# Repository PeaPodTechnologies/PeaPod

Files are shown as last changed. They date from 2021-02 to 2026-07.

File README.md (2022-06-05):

# PeaPod <!-- omit in toc -->

     

A cloud-connected isolated and automated plant growth environment, able to generate any environment from a combination of independent environment parameters. 

Designed as both a hassle-free food production system and a research tool for precise and distributed mapping of the plant-environment relationship.

<!-- TODO: Build statuses? etc. -->

Submitted to the [NASA/CSA Deep Space Food Challenge](https://impact.canada.ca/en/challenges/deep-space-food-challenge). _Update_: PeaPod has [won](https://impact.canada.ca/en/challenges/deep-space-food-challenge/semi-finalists) Phase 1 and moved on to prototyping for Phase 2!



***

### Table of Contents

- [Background](#background)
  - [Features](#features)
- [Production](#production)
- [Development](#development)
- [Contribution](#contribution)
  - [New Issue](#new-issue)
  - [Existing Issues](#existing-issues)
- [Acknowledgements](#acknowledgements)

<!-- include some visuals, i.e. a 3D GIF of the CAD, maybe a flowchart/diagram -->

***

## Background

See our [requirements document](https://github.com/PeaPodTechnologies/PeaPod/blob/staging/docs/requirements/Requirements.pdf).

### Features

See our [progress report](https://github.com/PeaPodTechnologies/PeaPod/blob/staging/docs/RrogressReport.pdf).

<!-- ### Innovations
PeaPod is *not* a fancy container with a light stand. 

PeaPod can **precisely** replicate climates for optimal growing conditions, and also has the ability to collect plant growth data during the growing cycle. 
This data is then used to further *optimize climate parameters* so food grown in PeaPods will taste better over time.

PeaPod is *modular* and *easy to assemble*. 
Construction with aluminum extrusion allows PeaPods to be transported like IKEA furniture, useful for situations where a lot of food is required at the end of a long journey. 
A lot of PeaPods can be collapsed into a tiny space. 
This also means PeaPods can be configured to be any size to grow any type of plant.

PeaPod is self-optimizing, versatile, easy to assemble, and it makes food. -->

***

## Production

<!-- ### Assembly

### Installation

w/ examples, i.e. GIF of expected output, inline code -->

TBA.

***

## Development
<!-- dependencies, environment, languages -->

> See [`software/README`](software/README.md#Development) and the individual [`subsystems`](/subsystems/README.md) for development details.

<br>

## Contribution

### New Issue

1. Open an issue with the features you'd like to add/bugs you'd like to see squashed (admins will add labels, assignments, etc.)
2. Discuss the scope and specifics in the issue, and either:
   1. Make a new branch, make changes, open a **PR Draft** (if you have permissions); or
   2. Fork this repo, make changes, open a **PR Draft**.
3. Request review by changing the **PR Draft** to a full-blown **PR** when you think it's ready.
4. If the reviewer(s) accept the changes, they will merge the **PR** and close the related issue.

### Existing Issues

Check out our [open issues](https://github.com/PeaPodTechnologies/PeaPod/issues?q=is%3Aopen+is%3Aissue+label%3A%22Status%3A+Open%22)!

<!-- ### Support -->
<!-- issues page, discussion board/Discord? -->

<br>

## Acknowledgements

Sincere thanks to the following individuals and groups:
- MIT Media Lab's Open Agriculture Initiative (for inspiration)
- The Open Source community
- Deep Space Food Challenge administrators and participants

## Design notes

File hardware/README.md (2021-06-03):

# PeaPod Hardware

Includes all bill of materials (BOM), 3D printing files, schematics, etc.

See [ASSEMBLY.md](../docs/assembly/ASSEMBLY.md) for fabrication and assembly instructions.

## References

Documentation for BOM parts can be found on each part's DigiKey page under "Datasheet".

# Development

BOM downloaded from [DigiKey](https://www.digikey.ca) (can be directly uploaded for ordering). 3D model files are made using [AutoDesk Fusion 360](https://shop.prusa3d.com/en/3d-printers/181-original-prusa-i3-mk3s-3d-printer.html). GCODE files are for the [Prusa MK3S+ MMU2](https://shop.prusa3d.com/en/3d-printers/181-original-prusa-i3-mk3s-3d-printer.html) using *Prusament PETG* filament. Schematics and PCB files made using [EasyEDA](https://easyeda.com/).

## Requirements

- Fusion 360 or your 3D editor of choice
- EasyEDA or your PCB/schematic editor(s) of choice
- Excel/Google Sheets or your CSV reader/spreadsheet software of choice

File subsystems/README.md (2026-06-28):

# PeaPod Subsystems

All subsystems will follow the same structure:

- `README.md` - Detailed instructions for fabrication and purchasing, list of materials incl. tools, assembly instructions with graphics, testing and validation protocol, method of operation, and expected results.
- `REQUIREMENTS.md`
- `assets/` - various graphical/etc. assets (diagrams, etc. excluding pictures of schematics/PCB layouts)
- `hardware/`
- `software/`

In addition, each subsystem should have its own `README.MD` with the following info:

- Purchasing
- Assembly w/ photos
- Testing (process and results)

## Hardware

Includes all **reference** bills of materials (BOM), 3D printing files, PCB files, etc.

Subdirectories:

- `boms/` - Bills of Materials (CSV files)
- `fabrication/` - Fabricated part files (i.e. 3D printing files)
- `schematics/` - PCB schematics (.SCH and .BRD files and photos of each)
- `gerber/` - Gerber files (PCB manufacturing)

## Software

Includes all C/C++ libraries and Arduino testing scripts.

Subdirectories:

- `src/` - Libraries
- `tests/` - Test scripts

# Development

Component BOMs downloaded from [DigiKey](https://www.digikey.ca) (can be directly uploaded for ordering). All other BoM types (fabrication, purchase, etc.) copied from the [BoM Templates](/.github/BOM_TEMPLATES/). 3D models, PCB and schematic docs are made using [AutoDesk Fusion 360](https://www.autodesk.ca/en/products/fusion-360/overview).

## Requirements

- Fusion 360 or your 3D editor of choice
- EasyEDA or your PCB/schematic editor(s) of choice
- Excel/Google Sheets or your CSV reader/spreadsheet software of choice

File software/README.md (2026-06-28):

# PeaPodOS <!-- omit in toc -->
 
A two-part system, consisting of a high-level software application and a low-level microcontroller firmware, designed for remote monitoring and configuration of control systems.

The software is written in TypeScript and runs on any compatible computer system with an internet connection, persistent storage, and a UART serial interface (i.e. Raspberry Pi Zero 2 W).

The firmware is written in Arduino C++ and runs on any compatible microcontroller system with UART serial and I2C interfaces (i.e. Adafruit ESP32 Feather V2). See `./microcontroller/README.md` for more information.

Ensure UART voltage levels are compatible (i.e. 3.3V for both Raspberry Pi Zero 2 W and Adafruit ESP32 Feather V2).

### Table of Contents
- [Background](#background)
- [Architecture](#architecture)
- [Development](#development)
- [Production](#production)
  - [Raspberry Pi Zero 2 W](#raspberry-pi-zero-2-w)
    - [SD Card Preparation](#sd-card-preparation)
    - [First-Time Setup](#first-time-setup)
  - [Preparation](#preparation)
  - [Installation](#installation)
  - [Execution](#execution)

# Background

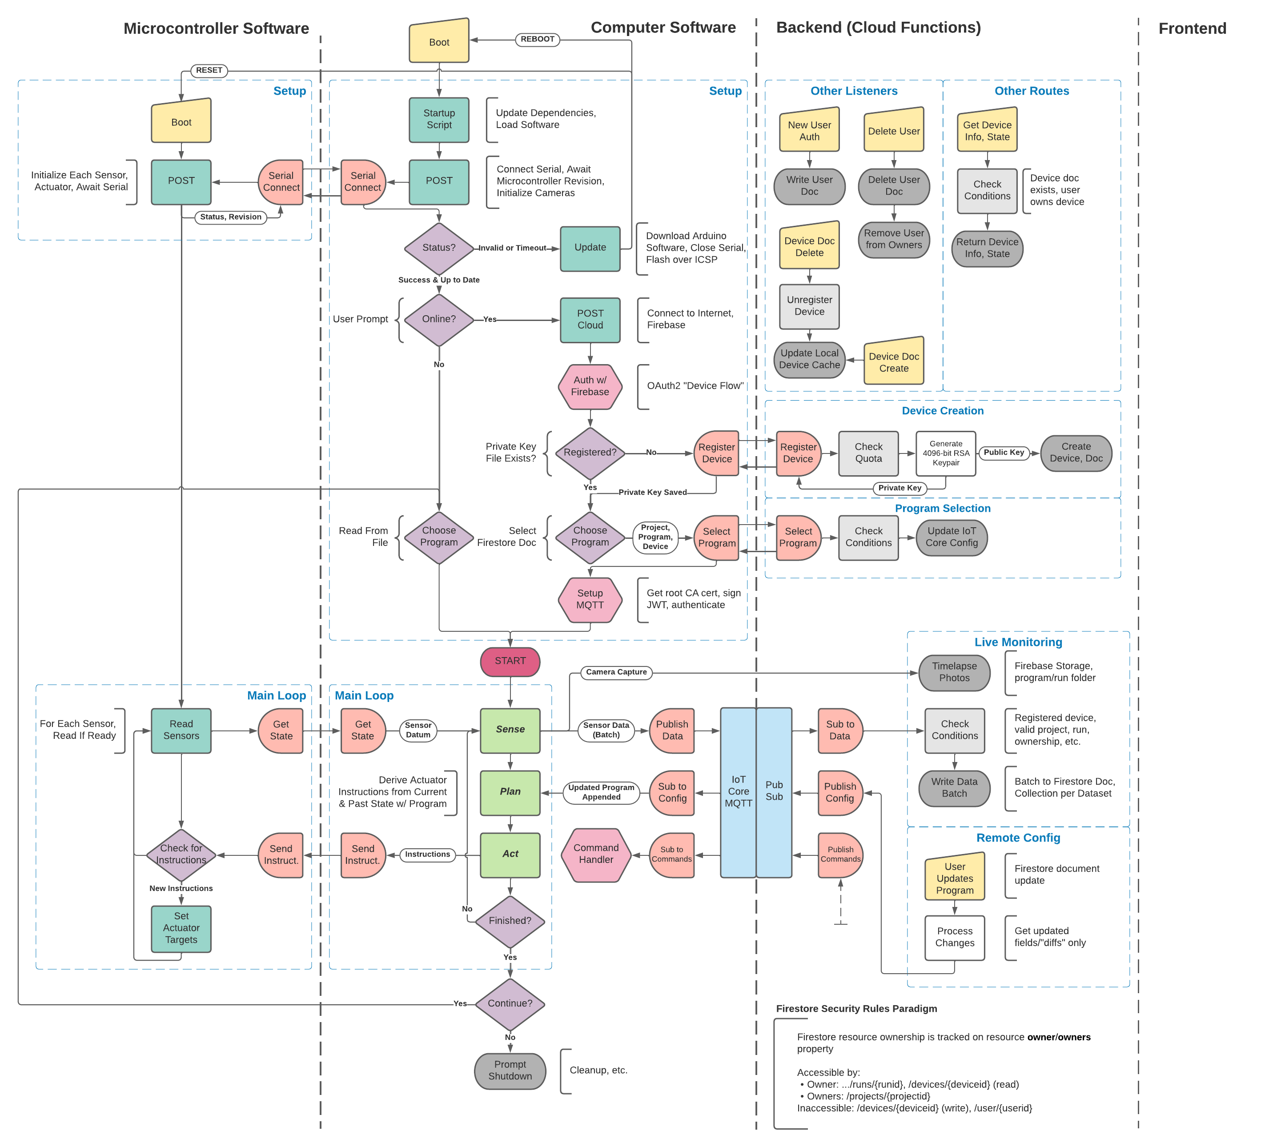
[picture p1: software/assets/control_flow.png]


# Architecture

start menu
- publishing mode selection (Local Filesytem, Firebase, Dashboard)
- Firebase Device Flow Authentication
  - Provider Selection (Google, GitHub)
  - Device Code & URL
- Microcontroller Serial Port Selection

serial communication
- bidirectional
- JSON-formatted
- newline-delimited
- encoding: device commands, system configuration
- decoding: telemetry/debugging

WebSockets API w/ Callbacks
- camera capture and image streaming
- serial passthrough
- intervals
- linker
- firmware flashing
- scheduler

Control Systems (TODO)

dashboard webserver
- Debugging Console
- Telemetry Charts
- Calendar + DataGrid
- Interval & Event Scheduler
    - Microcontroller Instructions
    - Tasks

# Development

# Production

## Raspberry Pi Zero 2 W

### SD Card Preparation

The following are performed on a computer with an internet connection:

1. Format a microSD card (>=32GB) with a single FAT partition.
2. Download the Raspberry Pi Imager [(Download)](https://www.raspberrypi.com/software/).
3. Flash the SD card with a *Raspberry Pi OS Lite (64-bit)* image.

> Note: A custom PeaPodOS image will be released in the future.

### First-Time Setup

4. Plug in a keyboard and display, insert the microSD card, and power on the Raspberry Pi Zero 2 W.

The following are performed on the Raspberry Pi Zero 2 W, with a keyboard and monitor:

5. Login.
6. Execute `sudo raspi-config` and perform these steps to setup the Pi:
   1. *System Options > Wireless Lan* - Setup WiFi and connect to the Internet (if not set from within imager)
   2. *System Options > Hostname* - Set a unique hostname, e.g. `peapod` (if not set from within imager)
   3. *System Options > Boot/Auto Login* - Select `Console Autologin` (B2)
   4. *Interface Options > SSH* - `Enable` SSH Server (if not set from within imager)
   5. *Interface Options > Serial Port* - `Disable` serial login shell, but `Enable` the serial port hardware
   6. *Performance Options > GPU Memory* - 256 MB (to support the camera module, if used)
   7. *Localisation Options > Locale* (i.e. `en_US.UTF-8`)
   8. *Localisation Options > Timezone* (i.e. `US` > `Eastern`)
   9. *Localisation Options > Keyboard* (i.e. `Generic 105-key` > `English (US)` > `Default` > `No compose key`)
   10. Optional: *Advanced Options > Expand Filesystem*
   11. Reboot to save: `sudo reboot -f` 

> You can now SSH into the Raspberry Pi to perform the rest of the setup, or continue with the keyboard and monitor.

## Preparation

The following are performed on a computer with an internet connection:

7. Execute `./scripts/build.sh` WITH NO ARGUMENTS to compile TypeScript to JavaScript and bundle the webserver, creating an `./out.tar.gz` archive containing the compiled software.
8. Execute `./scripts/upload.sh <hostname>` to upload the `./out.tar.gz` archive to the Raspberry Pi Zero 2 W home directory, where `<hostname>` is the hostname of the Raspberry Pi (e.g. `peapod.local`).

> You may need to use `chmod +x ./scripts/*.sh` to make the scripts executable.

## Installation

9. Update package listings, upgrade existing packages: `sudo apt update && sudo apt full-upgrade -y`

10. Install Node.JS, the Node package manager, and Python dependencies: `sudo apt install -y nodejs npm python3-venv python3-dev`
<!-- 3. Install main software package: `sudo npm i -g @peapodtech/peapodos --save` -->
<!-- 4. If using a Raspberry Pi Camera, install the camera package: `sudo apt install -y libcamera-apps` -->

11. Install [PlatformIO Core](https://docs.platformio.org/en/latest/core/installation/methods/installer-script.html#super-quick-macos-linux)
<!-- 
1. Create a custom configuration file for the AVR flash utility *avrdude* to be able to program the Arduino Nano via ICSP over the Raspberry Pi's GPIO pins:
   1.  Create a local copy of the *avrdude* configuration file with `cp /etc/avrdude.conf ~/avrdude_gpio.conf`, then modify your copy with `nano ~/avrdude_gpio.conf`. Copy the following to the end of the file:

       ```
       # Raspberry Pi GPIO configuration for avrdude.
       programmer
         id    = "peapod";
         desc  = "Use the Linux sysfs interface to bitbang GPIO lines";
         type  = "linuxgpio";
         reset = 5;
         sck   = 6;
         mosi  = 12;
         miso  = 13;
       ;
       ```
       (*Ctrl-O* to save, *Ctrl-X* to exit)
   2.  Verify the configuration and connection to the Arduino with `sudo avrdude -p m328p -C/avrdude_gpio.conf -c peapod -v`. A successful output should look something like:
       ```
       avrdude: Version 6.3-20171130
            Copyright (c) 2000-2005 Brian Dean, http://www.bdmicro.com/
            Copyright (c) 2007-2014 Joerg Wunsch

            System wide configuration file is "/home/pi/avrdude_gpio.conf"
            User configuration file is "/root/.avrduderc"
            User configuration file does not exist or is not a regular file, skipping

            Using Port                    : unknown
            Using Programmer              : peapod
            AVR Part                      : ATmega328P
            Chip Erase delay              : 9000 us
            PAGEL                         : PD7
            BS2                           : PC2
            RESET disposition             : dedicated
            RETRY pulse                   : SCK
            serial program mode           : yes
            parallel program mode         : yes
            Timeout                       : 200
            StabDelay                     : 100
            CmdexeDelay                   : 25
            SyncLoops                     : 32
            ByteDelay                     : 0
            PollIndex                     : 3
            PollValue                     : 0x53
            Memory Detail                 :

                                     Block Poll               Page                       Polled
              Memory Type Mode Delay Size  Indx Paged  Size   Size #Pages MinW  MaxW   ReadBack
              ----------- ---- ----- ----- ---- ------ ------ ---- ------ ----- ----- ---------
              eeprom        65    20     4    0 no       1024    4      0  3600  3600 0xff 0xff
              flash         65     6   128    0 yes     32768  128    256  4500  4500 0xff 0xff
              lfuse          0     0     0    0 no          1    0      0  4500  4500 0x00 0x00
              hfuse          0     0     0    0 no          1    0      0  4500  4500 0x00 0x00
              efuse          0     0     0    0 no          1    0      0  4500  4500 0x00 0x00
              lock           0     0     0    0 no          1    0      0  4500  4500 0x00 0x00
              calibration    0     0     0    0 no          1    0      0     0     0 0x00 0x00
              signature      0     0     0    0 no          3    0      0     0     0 0x00 0x00

            Programmer Type : linuxgpio
            Description     : Use the Linux sysfs interface to bitbang GPIO lines
            Pin assignment  : /sys/class/gpio/gpio{n}
              RESET   =  8
              SCK     =  11
              MOSI    =  10
              MISO    =  9

       avrdude: AVR device initialized and ready to accept instructions

       Reading | ################################################## | 100% 0.00s

       avrdude: Device signature = 0x1e950f (probably m328p)
       avrdude: safemode: lfuse reads as FF
       avrdude: safemode: hfuse reads as DA
       avrdude: safemode: efuse reads as FD

       avrdude: safemode: lfuse reads as FF
       avrdude: safemode: hfuse reads as DA
       avrdude: safemode: efuse reads as FD
       avrdude: safemode: Fuses OK (E:FD, H:DA, L:FF)

       avrdude done.  Thank you.
       ``` -->

<!-- 11. Edit the `sudoers` file to allow `avrdude` to be executed using `sudo` *without a password*:
    1.  Open the `sudoers` file: `sudo visudo`
    2.  Add the following line to the end (assuming your username is `pi`, the hostname is `peapod`, and the `avrdude` binary is located at `/usr/bin/avrdude`):
        
        `pi peapod = (root) NOPASSWD: /usr/bin/avrdude`
        
        (*Ctrl-O* to save, *Ctrl-X* to exit; *avrdude* can be located with `whereis avrdude`) -->

<!-- 12. Install the *UV4L* camera library:
    1.  `curl https://www.linux-projects.org/listing/uv4l_repo/lpkey.asc | sudo apt-key add -`
    2.  Add the package listings: `echo "deb https://www.linux-projects.org/listing/uv4l_repo/raspbian/stretch stretch main" | sudo tee /etc/apt/sources.list.d/uv4l.list`
    3.  Update packages: `sudo apt-get update`
    4.  Install the core library, the Raspberry Pi driver, extra scripts, adn WebRTC support: `sudo apt-get install uv4l uv4l-raspicam uv4l-raspicam-extras uv4l-webrtc-armv6` -->

12.  Populate a `~/.env` file based on `./.env.template` with Firebase configuration, Google and/or GitHub auth configuration, serial port configuration, and webserver configuration (if applicable).

13. Unpack the `~/out.tar.gz` archive to the home directory: `tar -xzf ~/out.tar.gz -C ~`

14. Connect a USB cable from the computer (i.e. Raspberry Pi Zero 2 W) to the microcontroller (i.e. Adafruit ESP32 Feather V2), and verify that the serial port is available and openable by executing `node ~/serialtest.mjs` and following the prompts. The serial port should be something like `/dev/ttyACM0` (NOT `/dev/ttyS0`, this is the GPIO UART).

15. Perform first-time microcontroller firmware flashing by executing `node ~/flash.mjs` and following the prompts. The serial port should be something like `/dev/ttyACM0` (NOT `/dev/ttyS0`, this is the GPIO UART).

## Execution

16. Run the main program by executing `node ~/server.mjs`.

18. Follow the prompts to select a publishing mode (Local Filesystem, Firebase, and/or Dashboard), and if applicable, perform Firebase Device Flow Authentication.

19. The webserver should start, making the dashboard accessible at the displayed hostname and port.

20. Select the appropriate serial port (i.e. `/dev/ttyS0` for GPIO UART-Arduino `Serial1`, `/dev/ttyACM0` for USB-Arduino `Serial`) to connect to the microcontroller.

21. The console will begin printing raw telemetry and debugging information from the microcontroller.

<!-- https://github.com/nebrius/raspi-io/wiki/Getting-a-Raspberry-Pi-ready-for-NodeBots#configuring-your-app-to-start-on-startup -->

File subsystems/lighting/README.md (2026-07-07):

# PeaPod Lighting Subsystem

See `./REQUIREMENTS.md` for the subsystem requirements.

Provides controlled light to the plant canopy and supports programmable photoperiods (on/off), light intensity (dimming), and spectral channel control via Adafruit PCA9685 PWM dimming of MEAN WELL LDD-L constant-current LED drivers powering CREE XLAMP LEDs with a variety of spectra, including PAR and white for imaging. Power regulator, I2C cables, and PCBs are documented swappable components.

# Production

## Assembly

### Bills of Materials

<!-- TODO: Cables?? -->

See `./hardware/lighting_bom_purchase.csv` for the purchase bill of materials. See `./hardware/gerber/` for PCB manufacturing files (NOTE: STENCIL NECESSARY). See `./hardware/lighting_bom_components.csv` for the electronic components bill of materials (DigiKey).

1. 1 x Lighting BOM Components per led board
2. 1 x Lighting BOM Purchase per led board

### Tools and Equipment

Required:
- Soldering Iron, Solder, and Flux
- Wire Strippers (20-30 AWG)
- Reflow Oven (or hot air rework station) and solder paste
- Putty Scraper

Optional, but recommended:
- Helping Hands (for soldering)
- Multimeter (for testing connections)
- Oscilloscope (for testing signal integrity)
- Luminous Flux Meter (for measuring light output)

## Instructions

1. Using a putty scraper, apply solder paste to the PCB using the stencil.
2. Place the surface-mount components (signal connector, resistor, and LEDs) on the PCB according to the silkscreen.
3. Reflow the PCB in a reflow oven (or use a hot air rework station) to solder the surface-mount components.
4. Solder the through-hole components (power connector and LED driver) to the PCB according to the silkscreen.

## Testing

### Power Test

**Protocol**: Connect the 24V power supply (+24VDC and GND) to the power connector on the PCB.

**Validation**: Nothing happens. Test points TP3 and TP4 read +24V and 0V, respectively.

**Failure Protocol**: 

1. *Smoke, Sparks or Unusual Heat/Odors*: Immediately disconnect the power supply. Check the PCB for solder bridges or shorts. If issue persists, check the power supply and ensure it is functioning correctly.

2. *Incorrect Voltage Readings*: Check the power supply connections and ensure the PCB is properly soldered.

### LED Light Test

**Protocol**: Connect the 24V power supply (+24VDC and GND) to the power connector on the PCB. Flash an Arduino-compatible microcontroller with the `./software/tests/Test_SingleWave/Test_SingleWave.ino` sketch. Connect the microcontroller to the signal connector on the PCB (Digital Pin 3 and GND). Observe the behavior of the LEDs.

**Validation**: The LEDs should light up in a sinusoidal wave pattern, with the brightness varying smoothly over time.

**Failure Protocol**: Check the power supply connections and ensure the PCB is properly soldered. Check test points TP3 and TP4 for correct voltage levels. Check the microcontroller connections to the signal connector and ensure the correct pin is used. Check test point TP5 for PWM signal using an oscilloscope. If issue persists, check the microcontroller code and ensure it is functioning correctly.

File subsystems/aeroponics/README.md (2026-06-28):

# Aeroponics Subsystem

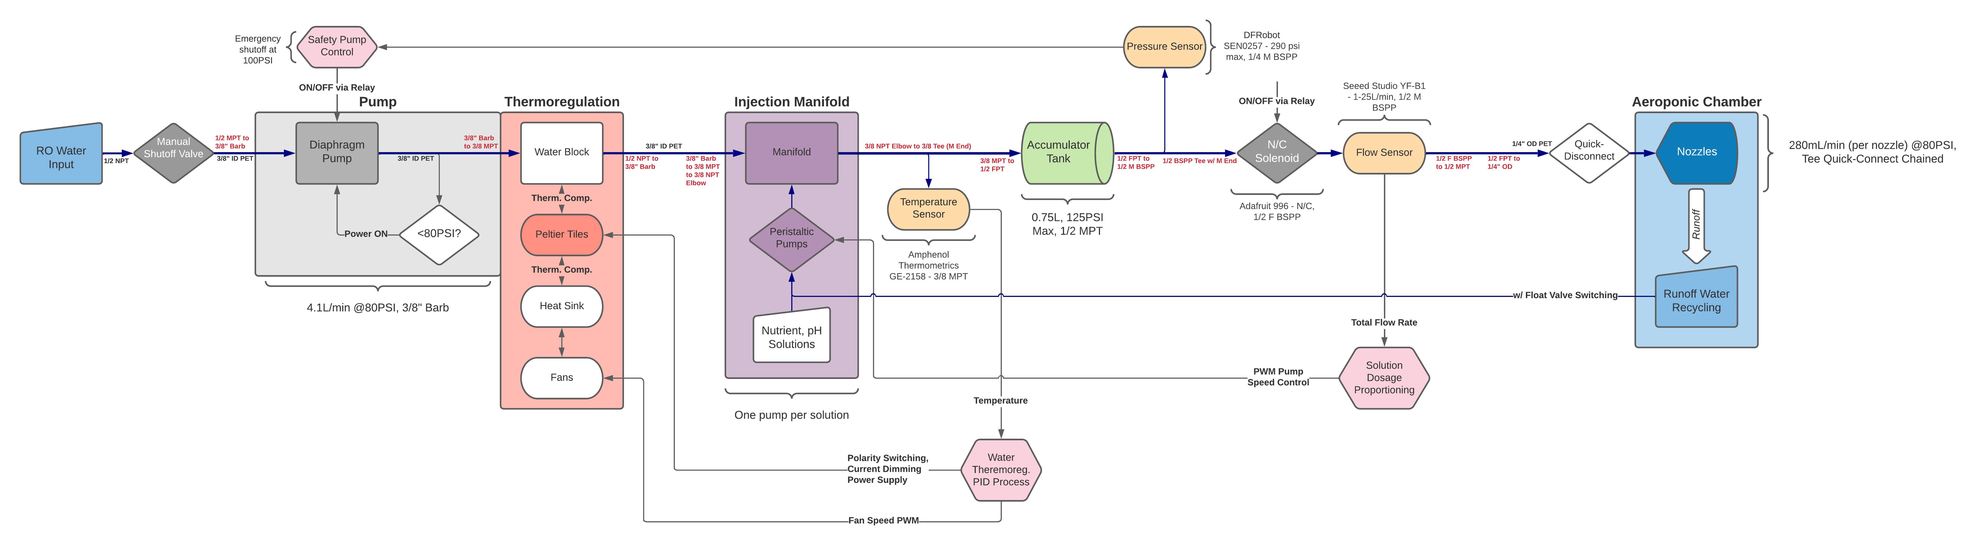
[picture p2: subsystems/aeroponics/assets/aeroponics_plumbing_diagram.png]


# Assembly

## Assembly Notes

Review these before assembly.

- Applying Teflon Tape: [Tutorial](https://www.youtube.com/watch?v=f7mjyzfB9Ec)
- Assembling Compression Fittings: [Instructions](https://www.siouxchief.com/docs/default-source/technical-documents/installations/specialties/ander-lign-fittings-brass) (see pg. 2, Ander-Lign Universal Fittings)

## Materials

### Purchased

Refer to [the purchase BOM](./hardware/aeroponics_bom_purchase.csv).

### Tools

- Cutters (for tubing)
- Utility Knife (for Teflon)
- Pipe Wrench (for fittings)
- 12V Power Supply (for pump testing)

## Instructions

<!-- TODO: tubing lengths -->

> **NOTE**: Refer to the assembled photo below for orientations.

1. Cut a 30cm length of 3/8" PET tubing. Slide two hose clamps onto the tubing. Affix one end to the 3/4" Hose Female x 3/8" Barb fitting (**barb end**), and the other to the 3/8" *input* barb of the diaphragm pump (see photo). Secure one clamp firmly on each end.
3. Apply Teflon tape to the 3/8" Barb x 3/8" MPT Adapter (**MPT end**). Fit this adapter to the 1/2" x 3/8" FPT Coupling (**3/8" ends**). This assembly is now referred to as the *3/8"-1/2" Adapter*.
5. Cut a 30cm length of 3/8" PET tubing. Slide two hose clamps onto the tubing. Affix one end to the 3/8" *output* barb of the pump (see photo), and the other to the 3/8"-1/2" Adapter (**barb end**). Secure one clamp firmly on each end.
6. Cut a 30cm length of 1/4" OD PET tubing. Apply Teflon tape to the 1/4in. OD x 1/2in. MPT Compression Fitting Adapter (**MPT end**). *__DO NOT__ apply to the compression threads.* Assemble the compression fitting to the length of tubing. *__DO NOT__ over-tighten the compression nut.* Fit this adapter (**1/2" end**) to the 1/2" x 1/2" FPT Coupling. This assembly is now referred to as the *1/2"-1/4" OD Adapter*.
4. Apply Teflon tape to both 1/2" MPT ends of the accumulator tank. Affix the 3/8"-1/2" Adapter to the *input barb* of the accumulator tank. Affix the 1/2"-1/4" OD Adapter to the *output barb* of the accumulator tank.
5. Cut two 50cm lengths of 1/4" OD PET tubing. Insert the tubing from the 1/2"-1/4" OD Adapter into the push-connect input of the solenoid. Insert the first length of tubing into a) the push-connect output of the solenoid, and b) one of the "in-line" ends of a push-connect T-fitting. Insert the second length of tubing into a) the opposing "in-line" end of the push-connect T-fitting, and b) one end of a push-connect straight fitting.
6. Insert two nozzles into the open spots on the two push-connect fittings.

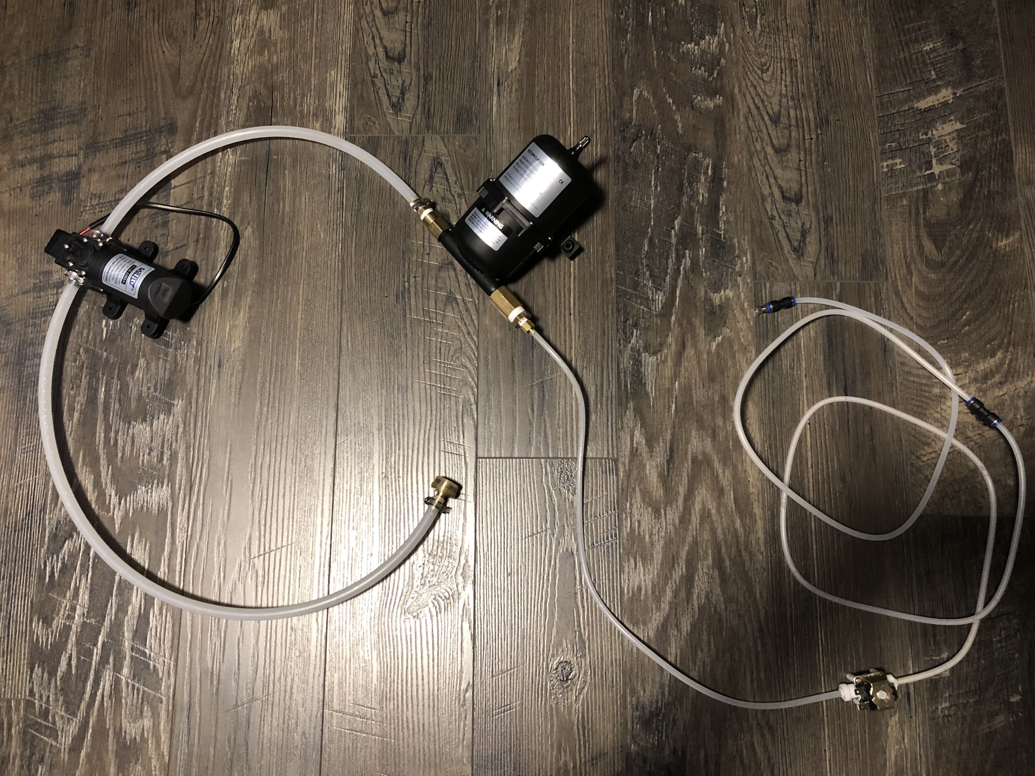
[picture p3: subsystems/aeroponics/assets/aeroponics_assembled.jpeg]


# Testing

> NOTE: As this is a pressurized system, the following tests should be done *in order*. Following the execution of each testing protocol, return the subsystem to the state following the completion of the assembly.

## Leaks

**Protocol**: Detach the solenoid and subsequent components. Attach a standard garden hose to the input end of the system. Turn on the water gradually, checking for leaks at each connection.

**Validation**: No leaks observed at any connection.

**Failure Protocol**: Disassemble the failed connection(s). Remove existing Teflon. Reapply Teflon, and reassemble the connection(s). Ensure Teflon is applied properly, and each connection is appropriately secured.

## Priming

**Protocol**: Fill a bucket with contaminant- and debris-free water. Ensure the system is on level ground. Place the input end of the system in the bucket. Detach the solenoid from the preceding tubing section. Detach the subsequent tubing section from the T-fitting. Connect the tank output tubing section to the T-fitting. Apply 12V power to the pump. *Priming may take a minute or two.*

**Validation**: The pump is able to prime the system and expel all air.

**Failure Protocol**: Ensure the system is level and the system input is submerged. Ensure the pump is receiving power.

## Pressurization

**Protocol**: Same as [Priming](#priming).

**Validation**: The system pressurizes without failure or leak at any connection or component.

**Failure Protocols** (in increasing order of severity): 

1. *Leak*: Depressurize the system. Disassemble the failed connection(s). Remove existing Teflon. Reapply Teflon, and reassemble the connection(s) tightly. Ensure Teflon is applied properly, and each connection is appropriately secured.
2. *Component Failure*: Replace the failed component. Repeat Assembly.

## Nozzle Function

**Protocol**: Same as [Priming](#priming).

**Validation**: Nozzle flow is uninterrupted and consistent in rate over time. Droplet size is as expected and consistent, both over time and across the range of droplets.

**Failure Protocol**: N/A

## Pump Auto-Shutoff

**Protocol**: Same as [Priming](#priming).

**Validation**: Pump shuts off automatically approximately one minute after priming is complete once pressurization is achieved. Nozzle flow is uninterrupted. Pump turns back on automatically to maintain pressure.

**Failure Protocol**: N/A

<!-- TODO: pressure sensor for accuracy -->

<!-- TODO: solenoid function -->

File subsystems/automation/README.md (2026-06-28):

# PeaPod Automation Subsystem

# Assembly

## Materials

### Purchased

See `./hardware/automation_bom_purchase.csv` for the purchase bill of materials. See `./hardware/gerber/` for PCB manufacturing files. See `./hardware/automation_bom_components.csv` for the electronic components bill of materials (DigiKey).

### Tools

Required:
- Soldering Iron, Solder, and Flux
- Wire Strippers (20-30 AWG)

Optional, but recommended:
- Helping Hands (for soldering)
- Multimeter (for testing connections)
- Oscilloscope (for testing signal integrity)

## Instructions

1. Solder stacking headers to the motherboard: one 2x20 at U1 for the Raspberry Pi Zero 2 W, and one each 1x16 and 1x12 at U2 for the Adafruit ESP32 Feather V2.
2. Solder 2x20 stacking header pins to the Raspberry Pi Zero 2 W, ensuring the pins are oriented to connect with the motherboard headers.
3. Solder 1x16 and 1x12 stacking header pins to the Adafruit ESP32 Feather V2 (if not pre-assembled), ensuring the pins are oriented to connect with the motherboard headers.
4. Prepare the micro-SD card according to the instructions in `/software/README.md` (using the SD card adapter). Insert the micro-SD card into the Raspberry Pi Zero 2 W.
5. Insert the Raspberry Pi Zero 2 W and Adafruit ESP32 Feather V2 into their respective headers on the motherboard, ensuring proper orientation (match footprint to the silkscreen).
6. Flash the Adafruit ESP32 Feather V2 with the `/software/microcontroller/` firmware according to the instructions in `/software/README.md`.
7. Assemble all subsystem modules in accordance with their instructions. Cut and strip four Qwiic wires, making eight one-ended connectors. Connect the modules to the Adafruit ESP32 Feather V2 I2C port using Adafruit Qwiic cables.
8. Optional: Mount the Adafruit 7-Segment Display Featherwing directly to the Adafruit ESP32 Feather V2 stacking headers.
9. Attach the small end of the orange-colored camera flex cable to the Raspberry Pi Zero 2 W camera port. Attach the large end to the coupling board. Attach one end of the long camera flex cable to the coupling board, and the other end to the camera module. Ensure that all cables are oriented such that the metal connectors on the cable are facing the PCB.
10. Connect a display to the mini-HDMI port on the Raspberry Pi Zero 2 W.
11. Connect the USB hub to the micro-USB port labelled "USB" on the Raspberry Pi Zero 2 W. Connect the keyboard to the USB hub.
12. Connect the power supply to the micro-USB port labelled "PWR" on the Raspberry Pi Zero 2 W.

# Testing

## Power-On Test

**Protocol**: Power on the system. Observe the behavior of the Raspberry Pi Zero 2 W via the connected display. Observe the behavior of the Adafruit ESP32 Feather V2 via the built-in LED (and 7-segment display and/or LCD display, if applicable).

**Validation**: The Raspberry Pi Zero 2 W boots successfully, as evidenced by the display output. The Adafruit ESP32 Feather V2 boots successfully, as evidenced by the LED behavior. 7-segment display and/or LCD display show expected output (if applicable): variable readout and "PeaPod Initializing...", respectively.

**Failure Protocol**: 

1. *Raspberry Pi Zero 2 W Fails to Boot*: Check power supply connection and ensure the micro-SD card is properly inserted. If issue persists, format and flash the micro-SD card according to the instructions in `/software/README.md` and repeat testing.
2. *Adafruit ESP32 Feather V2 Fails to Boot*: Check connections to the motherboard and ensure the board is properly seated in the header. If issue persists, reflash the Adafruit ESP32 Feather V2 using the appropriate firmware and repeat testing.

## Serial Communication Test

**Protocol**: Execute `yarn buildapi && node serialtest.mjs`. Select the appropriate serial port for the Adafruit ESP32 Feather V2 when prompted. Observe the output in the terminal.

**Validation**: The terminal outputs JSON-formatted sensor data at regular intervals (e.g. every second), as sent from the Adafruit ESP32 Feather V2.

**Failure Protocol**: 

1. *Serial Open Fails*: Check wiring connections to the motherboard and ensure the Adafruit ESP32 Feather V2 is properly seated in the header. Ensure no other applications are using the same serial port.
2. *No Data*: Check that the Adafruit ESP32 Feather V2 is running the appropriate firmware and is programmed to send serial data to the appropriate interface (i.e. Serial for USB vs. Serial1 for RX/TX UART). Check wiring connections to the motherboard and ensure the Adafruit ESP32 Feather V2 is properly seated in the header.

## Camera Test

**Protocol**: Execute `libcamera-hello -t 0`. Observe the output in the terminal and the connected display.

**Validation**: The terminal outputs a continuous stream of camera data, and the connected display shows the camera feed in real time.

**Failure Protocol**: Check camera flex cable connections to the Raspberry Pi Zero 2 W and coupling board, ensuring proper orientation. Ensure the camera module is properly connected to the coupling board. Check that the camera module is functional (e.g. by testing with another Raspberry Pi or camera board, if available). Ensure that the camera interface is enabled in the Raspberry Pi configuration settings.

## Firmware Flash Test

**Protocol**: Execute `pio run -t upload`. Observe the output in the terminal.

**Validation**: The terminal outputs messages indicating successful compilation and upload of the firmware to the Adafruit ESP32 Feather V2.

**Failure Protocol**:
1. *Compilation Fails*: Check that PlatformIO is properly installed and configured. Ensure that the correct board and environment are selected in the `platformio.ini` file. Review error messages for specific issues (e.g. missing libraries, syntax errors) and address accordingly.
2. *Upload Fails*: Check connections to the motherboard and ensure the Adafruit ESP32 Feather V2 is properly seated in the header. Ensure the correct serial port is selected for uploading. Check that the Adafruit ESP32 Feather V2 is in the appropriate mode for flashing (e.g. boot mode) and that any necessary drivers are installed.

## Dashboard Test

**Protocol**: Execute `yarn start`. Observe the output in the terminal and the connected display, and respond to prompts in the terminal as necessary to initiate the dashboard. Using a separate device on the same network, navigate to the appropriate local IP address and port number for the dashboard (e.g. `http://192.168.X.X:3000`). Observe the dashboard behavior and data readouts.

**Validation**: The terminal outputs messages indicating successful connection to the Adafruit ESP32 Feather V2 and receipt of sensor data. The separate device successfully loads the dashboard webpage, which displays real-time sensor data and updates appropriately.

**Failure Protocol**:
1. See *Serial Communication Test* failure protocols for issues related to serial communication between the Raspberry Pi Zero 2 W and Adafruit ESP32 Feather V2.
2. *Dashboard Fails to Load*: Ensure the separate device is on the same network as the Raspberry Pi Zero 2 W. Check that the correct local IP address and port number are being used to access the dashboard. Check for any firewall settings that may be blocking access to the port.
3. *Dashboard Loads but No Data*: Check the terminal output for any errors related to receiving or processing data from the Adafruit ESP32 Feather V2.

## Scheduler Test

**Protocol**: Execute `yarn start` and launch the dashboard. Add Event and Interval tasks using the floating action button with a plus icon. Observe the terminal output for scheduled task execution messages.

**Validation**: The terminal outputs messages indicating the execution of scheduled tasks at the appropriate times. States on the ESP32 Feather V2 change accordingly, as evidenced by the terminal output and dashboard readouts and hardware behaviour.

**Failure Protocol**:
1. *Tasks Not Executing*: Check that the scheduler code is properly implemented and that tasks are being added to the schedule correctly. Review terminal output for any errors related to task scheduling or execution.
2. *States Not Changing*: Check that the scheduled tasks are correctly sending commands to the Adafruit ESP32 Feather V2 and that the firmware on the Adafruit ESP32 Feather V2 is properly set up to receive and respond to these commands. Check wiring connections to the motherboard and ensure the Adafruit ESP32 Feather V2 is properly seated in the header.

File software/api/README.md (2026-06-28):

# API

- Node.JS Console i.e. limited-input devices
- WebSockets, SQL, File Logging, Firebase, etc.
-

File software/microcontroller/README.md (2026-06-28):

# PeaPod Microcontroller Firmware

Makes use of I2CIP, FSM, and DebugJson libraries for QOS-2 I2C device state management and abstraction, program state and control flow, and bidirectional JSON-formatted newline-delimited serial communication, respectively. Supports a main menu via 16x2 character LCD and rotary encoder with push button, and a seven segment display.

# Architecture

## Main

**Globals**:
- Menu State (menu index: enum, submenu index: unsigned char, selected module index: unsigned char)
- FSM:
  - Chronograph
- I2CIP:
  - modules\[8\]
  - errlev\[8\]

**Setup**:

1. Initialize Serial communication (115200 baud).
2. Wait for Serial connection.
3. Instantiate PeaPod modules (Air, Watering, Lighting; See Module Callbacks).
4. Instantiate non-module devices:
   1. Seven-Segment Display (HT16K33)
   2. 16x2 Character LCD (JHD1313)
   3. Rotary Encoder with Push Button (Adafruit Seesaw)
5. Attach LCD print callback to menu state changes.
6. Print firmware `revision` to Serial.
7. Register callbacks:
   1. Cycle Callback (triggered on `Cycle` change):
      1. Set Chronograph to current time.
      2. Calculate and set `FPS`.
      3. Read Serial input (DebugJson) and route commands/config.
   2. Heartbeat Callback (Chronograph interval):
      1. Print `heartbeat` message to Serial.
      2. Print firmware `revision` to Serial.
      3. Print `FPS` to Serial.
      4. Print current `Cycle` to Serial.
   3. Module Callbacks (Chronograph interval):
      1. If MUX pings and module was not present, instantiate module. Add seven segment display where applicable. Call module-check call operator and set module error level.
      2. If MUX doesn't ping, set module error level.
      3. If error level indicates hardware has been lost, de-instantiate module.

**Loop**:

1. Increment `Cycle` (See Cycle Callback).
2. Read encoder input and update menu state.

**Subroutines**:

- onEncoderChange
- writeLCDMenu
- onEncoderPress

## Modules

### Base Module

> An abstract base class for PeaPod modules.

Defines one namespaced abstract Module class: `PeaPodModule`, that:
- has two private Hash Tables: one for storing registered Variables, and one for storing registered Flags,
- has a public method `registerVariable` for registering Variables to the module,
- has a public method `registerFlag` for registering Flags to the module,
- implements `deviceGroupFactory`, linking all device driver classes to the module,
- implements `handleCommand`, routing JSON `GASB` commands to devices by FQA,
- implements `handleConfig`, routing JSON key-value pairs to flags/variables by name,

### Air Module

> Monitors and controls air quality parameters such as temperature, humidity, and CO2 levels.

Defines three namespaced global Variables: `air_temperature`, `air_humidity`, and `air_co2`.

Defines three namespaced global Callbacks: `callback_temperature`, `callback_humidity`, and `callback_co2` that print the respective variable values to Serial when they are updated.

Defines one namespaced Module class: `PeaPodModuleAir`, that extends `PeaPodModule`, that:
- has two Chronograph intervals for reading sensors SHT45 and K30,
- defines two static callback functions for processing mean sensor readings from SHT45 and K30,
- on instantiation:
  - sets up the Chronograph intervals to read sensors at defined intervals and set the Variables,
  - sets up the Variable Callbacks to print updated values to Serial,
  - registers the Variables to the module.
- on destruction:
  - removes the Chronograph intervals from the Chronograph scheduler.

### Watering Module

> Controls the watering system.

Defines one namespaced global Flag: `enable_watering`.

Defines one namespaced Module class: `PeaPodModuleWatering`, that extends `PeaPodModule`, that:
- has two Chronograph intervals for setting the `enable_watering` flag to true and false, respectively,
- on instantiation:
  - sets up the Chronograph intervals to set/reset the `enable_watering` flag at defined intervals and phases,
  - sets up a Flag Callback to write on/off to a MCP23017 GPIO pin when the `enable_watering` flag is updated,
  - sets the `enable_watering` flag to false, setting the GPIO pin to off, and disabling the watering system,
  - registers the `enable_watering` Flag to the module.
- on destruction:
  - sets the `enable_watering` flag to false, setting the GPIO pin to off, and disabling the watering system,
  - removes the Chronograph intervals from the Chronograph scheduler.

### Lighting Module

> Controls the lighting system.

Defines three namespaced global Variables: `adc_voltage`, `pwm_lighting_red`, and `pwm_lighting_blue`.

Defines one namespaced global Flag: `enable_lighting`.

Defines two namespaced global Callbacks: `callback_adc_read` and `callback_adc_voltage` that read the ADC value and convert it to voltage, respectively.

Defines one namespaced Module class: `PeaPodModuleLighting`, that extends `PeaPodModule`, that:
- has three Chronograph intervals: one for reading the ADC, and two for setting the `enable_lighting` flag to true and false, respectively,
- defines two static callback functions: one for modulating the PCA9685 output based on PWM values and `enable_lighting` flag, and one for handling the `enable_lighting` flag updates (re-calling the PWM modulation callbacks),
- on instantiation:
  - sets up the Chronograph intervals to set/reset the `enable_lighting` flag at defined intervals and phases,
  - sets an initial value for the PWM channels,
  - sets up a Chronograph interval to read the ADC and set the `adc_voltage` variable,
  - sets up the ADC Variable Callbacks to read and convert ADC values to voltage and print to Serial,
  - sets up a Flag Callback to gate the PWM modulation based on the `enable_lighting` flag,
  - sets up two Variable Callbacks to modulate the PCA9685 outputs based on PWM values,
  - sets the `enable_lighting` flag to false, setting the PWM outputs off, and disabling the lighting system,
  - registers the Variables to the module,
  - registers the `enable_lighting` Flag to the module.
- on destruction:
  - sets the `enable_lighting` flag to false, setting the PWM outputs off, and disabling the lighting system,
  - removes the Chronograph intervals from the Chronograph scheduler.

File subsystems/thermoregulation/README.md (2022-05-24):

# PeaPod Thermoregulation Subsystem

## Purchasing

TODO: Notes on PCB ordering, multiple BoMs, etc.

## Assembly

## Testing

### Method

### Results

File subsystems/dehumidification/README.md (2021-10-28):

# PeaPod Dehumidification Subsystem

## Purchasing

## Assembly

## Testing

### Method

### Results

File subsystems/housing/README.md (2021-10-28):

# PeaPod Housing

## Purchasing

## Assembly

## Testing

### Method

### Results

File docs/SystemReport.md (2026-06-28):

# PeaPod System-Level Report

## Housing

**Purpose**: *Isolates* and *insulates* growth environment from surroundings (heat, light, water vapour, air). Provides structural integrity and mounting points for other subsystems, and enables system extendability via repeated "unit cell" topology.

**Method**:

 - *Setup*:
    1.  Assemble frame and insert panels;
    2.  Mount control module (w/ subsystems), connect inputs;
    3.  Install tray mounts, insert trays (w/ subsystems);

 - *Testing*:
    - Frame construction is rigid, level, and sturdy.
    - Panels are insulating against temperature changes, and mitigate water vapour loss.

 - *Process*:

    1.  Panels insulate against heat gain/loss, are opaque, and contain light and heat via reflection;
    2.  Shell construction is tight, thus sealing against moisture;
    3.  Internal vertical mounting channels for systems and horizontal plane "trays";
    4.  Self-contained control module with all subsystem supplies, as well as automation systems;
    5.  Solenoid lock to prevent unintended opening;
    6.  **Housing Extension** (can be repeated):
        1.  Add a second housing;
        2.  Remove dividing panel from both housings;
        3.  Join the two housings to form one larger 2x1 housing;
        4.  **Extension Modes** (may be combined in any way to suit
            application):
            - *Class 1* (no combined units, frame connection only): Leave the dividing panel, add a control module, and operate the two PeaPods **separately**.
            - *Class 2* (for 2-4 unit housing combinations): Operate the combined housing off **one** control module.
            - *Class 3* (for 5+ unit housing combinations): Add control modules to account for additional air volume, plant count, power requirement, etc. and operate in a **master-slaves topology**.

**Features**:

- *Control Unit*: Top-mounted self-contained unit encapsulating all system inputs (incl. power, water, network connection), subsystem supplies and controls (incl. power supplies, aeroponics supply i.e. pump and pressure vessel and solenoid, thermoregulation control, humidity control, gas composition and exchange, and automation systems).

- *Frame*: T-slotted 2020 aluminum extrusion framing with face-mounted brackets forms a cubic skeleton for rigidity/strength (high strength-to-weight aluminum) and easy component mounting and repositioning. These extrusions form the edges of the cubic housing.

- *Panels*: Graphite-enhanced expanded polystyrene (GPS) rigid foam insulation panels with reflective mylar internal lamination increase energy efficiency (GPS RSI of 0.0328$\frac{m^2 \cdot \degree C}{W}$ per mm of thickness, mylar enables light/heat reflection), as well as safety against cross-contamination and pathogens. Panels press-fit into the frame and form a seal for greater water vapour retention.

- *Solenoid Lock*: Normally-open solenoid lock engages on-demand to prevent unintended contact with environment. Controlled by a relay. Mitigates cross-contamination and maintains environment accuracy.

- *Grow Trays*: Horizontal plane subframes mounted to internal vertical extrusion channels for ease of leveling and repositioning. Trays slide in/out on drawer slides mounted to front-back-horizontal DIN rails. All electrical and water connections are quick-disconnect for ease of tray removal.

- *Lighting Units*: Arrays of LED strips mounted to left-right-horizontal DIN rails (which also support top-down cameras).

## Aeroponics

**Purpose**: Delivers plant nutrients and pH- and temperature-controlled water to the roots via a fine mist.

**Function**:
- **Inputs**: Reverse osmosis water under positive pressure (pre-dosed with nutrient solutions and pH-balanced), nozzle delivery on/off control, water thermoregulation control signal
- **Outputs**: pH- and nutrient-balanced water mist (50 micron mean droplet diameter)

**Method**:

 - *Setup*:
    1.  Connect water input to the supply unit;
    2.  Connect supply unit to the supply pump input;
    3.  Connect runoff recapture line to the supply unit (for recycling) or to drain;
    4.  Connect the quick-disconnect fittings to the grow tray;
    5.  Calibrate pressure, temperature sensors;
    6.  Enable water input to prime system;
    7.  Mount aeroponic container to tray, ensure drawstring seal is fitted to the extrusion channel;

 - *Testing*:
    - Temperature, pressure sensors communicate as expected.
    - No leaks at any component under a) source pressure, b) fully pressurized.
    - Supply pump actuates and auto-shuts off as expected, and is able to deliver the required pressure.
    - All components, tubing, and connectors/fittings withstand full pressurization.
    - Solenoid is normally closed, withstands full pressurization, and opens when power is applied.
    - Quick-disconnect operates as intended at full pressurization without leaks.
    - Nozzles produce even-distribution full-cone mist.
    - Runoff container is sealed, and runoff collection operates as intended.

 - *Process*:
    1.  Water source fills supply unit (manual);
    2.  Nutrient solutions and pH balancers are dosed into supply unit as
        necessary (manual);
    3.  Heat is added to the water;
    4.  Water is pressurized to constant 80psi;
    5.  Temperature and pressure of the water is read (feedback);
    6.  Flow to nozzle is controlled (on/off);
    7.  Nozzle turns pressurized water into mist;
    8.  Runoff is contained by a water-tight container, and recaptured for
        recycling or draining;

**Features**:

- *Water Source* (EXTERNAL DEPENDENCY): A source of reverse osmosis water.
- *Supply Unit*: A coated-steel bucket with a lid holds reverse osmosis water for dosing with nutrient solutions and pH-balancing. Features an adhesive-back heat pad with thermostat.
- *Supply Pump*: Self-priming diaphragm pump, auto-shutoff at 80psi. Power is controlled by a relay.
- *Water Temperature Sensor*: Tee-fitted. Informs the heat pad thermostat.
- *Pressure Vessel*: Uses an air bladder to maintain and stabilize pressure.
- *Pressure Sensor*: Allows for shutoff of pump in case of emergency.
- *Drain Valve*: Tee-fitted ball valve. Allows the system to be depressurized and drained.
- *Solenoid Valve*: Controls delivery to the nozzles to enable on-demand misting.
- *Grow Tray Quick-Disconnect*: One each for watering line and runoff recapture line. Enables quick disconnection with auto-shutoff so the trays may be removed.
- *Nozzle*: Mounted to underside of grow tray, pointed at plant roots. 80psi water through a 0.4-0.6mm orifice produces ~50 micron water droplets, optimal for plant growth.
- *Root-Zone Container*: Watertight container that encapsulates the entire root zone. Made of a woven waterproof composite fabric (CT5K.18 mylar with Dyneema, 33.89g/m^2), chosen for high strength-to-weight ratio (15x that of steel) and natural no-coating food-safe waterproof quality. Mounted and **sealed** to the grow tray with a drawstring for easy root zone access.
- *Runoff Collection Pump*: Small sump pump to recapture runoff water for recycling or draining. Auto-activated when water is detected in the root-zone container (built-in float switch).

## Leaf-Zone Thermoregulation

**Purpose**: Maintaining desired leaf-zone air temperature and circulating air.

**Function**:
- **Inputs**: Power, air temperature control signal, air circulation control signal
- **Outputs**: Heat to/from system, by-product heat from/to surroundings, internal air circulation, internal air temperature sensor readings

**Method**:

 - *Testing*:

    - Heat pump direction and magnitude respond to control signal as expected;
    - Fans operate as expected;
    - Heat pump power exceeds maximum heat transfer at system temperature extremes;
    - Heat pump power exceeds that required to reach temperature extremes in under 120 seconds given the system’s heat capacity;

 - *Process*:

    1.  Air is circulated throughout the environment;
    2.  Temperature is measured, sent to automation system;
    3.  Control module controls heat pump speed and direction (heating vs. cooling system);

**Features**:

- *Circulation Fans*: Located in growth environment to circulate air for even temperature distribution, rapid system flushing, and automatic pollination.
- *Temperature Sensors*: Multiple temperature and humidity sensors frame-mounted throughout the growth environment to measure air temperature. Informs the **PID control loop**.
- *Heat Pump*: Pumps heat in or out of the growth environment. Is comprised of:
  - *Peltier Device*: 85W bidirectional solid-state **thermoelectric device** (aka Peltier tile) pumps heat from one face to the other. Better space efficiency, less complexity (no liquids, pressurized fluids, etc.), and more precise than other methods.
  - *Thermoelectric Driver Board*: Controls *magnitude* and *direction* of heat transfer via a **dimmable voltage source** (low-pass-filtered PWM to a voltage buffer and amplifier w/ feedback) and **relay H-bridge**, respectively.
  - *Heat Sinks*: Aluminum blocks with fins hold and exchange heat between air and Peltier devices. One set on each side of the Peltier (inside and outside environment) builds "heat pump". Mating face coated with thermal compound for better transfer.
  - *Heat Sink Fans*: Located on both sets of heat sinks for better heat dissipation.
- *PID Control Loop*: A propotional-integral-derivative control loop enables increased accuracy. Temperature sensors inform the loop, "error" is calculated (current vs desired temperature), and this informs the magnitude and direction of heat pump control. Requires tuning of parameters. Built into the automation system.

## Leaf-Zone Humidity Regulation

**Purpose**: Regulates the relative humidity of the leaf zone.

**Function**:
- **Inputs**: Humidification on/off control signal, dehumidification on/off control signal
- **Outputs**: Humidification or dehumidification on-demand

**Method**:

 - *Process*:
    1.  When humidity is too low (below dead-zone), humidification is activated;
    2.  When humidity is too high (above dead-zone), dehumidification is activated;
    3.  When humidity is at target (within dead-zone), both systems are deactivated;

**Features**:

- *Humidification System*
- *Dehumidification System*
- *Humidity Sensors*: Multiple temperature and humidity sensors frame-mounted throughout the growth environment to measure air relative humidity (%RH). Informs the **bang-bang control loop**.
- *Bang-Bang Control Loop*: A bang-bang (on/off) control loop with a hysteresis dead-zone. Humidity sensors inform the loop, "error" is calculated (current vs desired humidity), and this informs whether or not to activate either the humidification or dehumidification systems (or neither). Requires tuning of dead-zone (automatic). Built into the automation system.

### Humidification System

**Purpose**: Actively *increases* growth environment air humidity.

**Function**:
- **Inputs**: Power, humidification on/off control signal, reverse osmosis water
- **Outputs**: Dry water vapour

**Method**:

 - *Setup*:
    1.  Connect humidification control signal to control module.
    2.  Fill water tank.

 - *Testing*:
    - Humidification unit responds to control signal as expected;
    - Humidity sensor reads as expected;
    - Tank does not leak;

 - *Process*:
    1.  Water is delivered to a small tank (nebulizer is mounted);
    2.  Power and control signal activate a nebulizer driver;
    3.  Nebulizer vapourizes water;

**Features**:

- *Circulation Fans*: To circulate dry water vapour for even humidification.
- *Humidification Unit*: Easily controllable and produces a consistent vapour. Comprised of:
  - *Water Tank*: Holds a small amount of water behind the piezoelectric mesh.
  - *Mesh Nebulizer*: Piezoelectric ceramic disc with a microporous stainless steel mesh in the center. Oscillates in such a way that dry vapour is generated when water is passed over the mesh. Mounted to the water tank.
  - *Driver Circuit*: Fixed-frequency 555 timer circuit driving an amplifier/LC circuit generates an sinusoidal signal. Powers the piezoelectric disc.

### Dehumidification System

**Purpose**: Actively *decreases* growth environment air humidity.

**Function**:
- **Inputs**: Humid air (high water vapour content), dehumidification on/off control signal, dry desiccant
- **Outputs**: Dry air (low water vapour content), saturated desiccant, desiccant saturation level signal

**Method**:

 - *Setup*:
    1.  Connect dehumidification control signal to control module;
    2.  Insert dry desiccant cartridge;

 - *Testing*:
    - Desiccant removes moisture from air.
    - Desiccant indicates saturation as expected, which is sensed by computer.
    - Shutters operate as intended, and no dehumidification occurs when closed.
    - Maximum dehumidification rate exceeds total plant transpiration rate.

 - *Process*:
    1.  Dehumidification control signal activates fans and opens shutters;
    2.  Humid air passes over the desiccant, and dry air exits the unit;
    3.  Desiccant becomes saturated, and indicates degree of saturation;
    4.  Indication is sensed by computer, which notifies the user when to replace and dehydrate/"recharge" desiccant;

**Features**:

- *Dehumidification Unit*: One input port and one output port. Comprised
  of:
  - *Fans*: Humidity-rated fans force moist air through the desiccant cartridge input port and dry air out of the output port.
  - *Filter*: Polyethylene-polyropylene blend (non-toxic) MERV 13 (0.3 micron) air filters located at input and output ports of dehumidification chamber eliminate risk of any airborne pathogens being transferred onto silica beads and out of the system during cartridge recharging.
  - *Shutters*: Servo-actuated shutters enable opening and closing of dehumidifier input and output on demand. Air-tight when closed to prevent unintended dehumidification.
  - *Desiccant Cartridge*: Oven-safe. Easily removable for swapping and "recharging". Contains the silica gel desiccant.
  - *Indicating Silica Gel Desiccant*: Cheap, efficient, food-safe, reusable chemical desiccant beads with a water mass capacity of 6%. Changes color from blue to pink when saturated.
- *Color Sensor*: Optical color sensor senses cartridge saturation. Informs when to recharge the desiccant cartridge.
- *Evaporator Oven* (EXTERNAL DEPENDENCY): A ventilated oven that can maintain 125°C for 12 hours. Heats cartridge to evaporate/"bake off" moisture collected by silica beads, thus "recharging" them.

## Gas Composition Regulation and Exchange

**Purpose**: Controls gas composition of the growth environment by mediating exchange with surroundings.

**Function**:
- **Inputs**: Power, exchange control signal (open/closed and exchange rate)
- **Outputs**: Gas intake (from surroundings), gas exhaust (to surroundings; filtered and humidity-controlled)

**Method**:

 - *Setup*:
    1.  Connect exhaust port to onboard filtration/dehumidification system;
    2.  Connect shutter servos, fans to control module;

 - *Testing*:
    - Shutter servos, fans operate as intended.
    - Ports are air-tight when closed.
    - Exhaust filter removes all aerosols (i.e. pollen, seeds) and pathogens.
    - Exhaust dehumidification brings humidity down to ambient (~60%).

 - *Process*:
    1.  On-demand, intake and exhaust ports activate. Shutters open, and fans are enabled;
    2.  Intake port draws in air from surroundings;
    3.  Exhaust port expels air through filtration and dehumidification systems to be recycled;

**Features**:

- *Exchange Port*: Intake and exhaust, normally sealed. Each comprises:
  - *Shutters*: Servo-actuated shutters enable opening and closing of ports on demand. Air-tight when closed.
  - *Fan*: Humidity-rated fans control gas intake and exhaust rates.
  - *Filter*: Polyethylene-polyropylene blend (non-toxic) MERV 13 (0.3 micron) air filters eliminate risk of any airborne pathogens being transferred into or out of the system during gas exchange.

- *Gas Concentration Sensors*: A variety of sensors frame-mounted in the growth environment collect data on concentrations (ppm) of relevant gasses (CO2, O2, etc.). Informs the **bang-bang control loops**.
- *Bang-Bang Control Loops*: Maintains gas concentrations to within desired ranges.
- *Output Dehumidifier*: **Onboard life support systems** provides a dehumidifier (as well as additional filtration) to mitigate exhaust humidity.

## Lighting

**Purpose**: Discrete light spectrum and intensity control to provide all light necessary for plant growth, as well as sanitization.

**Function**:
- **Inputs**: Power, lighting spectrum-intensity control signal (aka per-LED modulation signals)
- **Outputs**: Spectrum and intensity controlled light

**Method**:

 - *Setup*:
    1.  Connect power and spectrum-intensity control signal to LED board onboard drivers.
    2.  Mount LED boards to lighting unit.

 - *Testing*:
    - Spectrum-intensity distribution control signal modulates LED power as expected;
    - Passive heat sinks dissipate enough heat;

 - *Process*:
    1.  Power is delivered to drivers;
    2.  Control signals "dim" drivers to modulate intensity distribution across spectrum;
    3.  Power drivers power LEDs;
    4.  LEDs emit light;

**Features**:

- *LED Lights*: LEDs offer high power output, better efficiency and thermal management, lower footprint, and precise wavelengths while minimizing risk of damaging plant tissues. Many discretely-controlled wavelength options/"series" enable wide and fine control of intensity-spectrum distribution, with a focus on Photosynthetically-Active Radiation (PAR), as well as sanitization wavelengths and wavelengths to induce specific phenotypic and chemical changes. Located across multiple smaller daisy-chained PCBs to minimize cost. LED series include:
  - Ultraviolet (267nm) for sanitization;
  - Blue (448nm);
  - Cool White (5700K);
  - Warm White (2700K);
  - Red (645nm);
  - Near-Infrared (730nm);

- *LED Power Drivers*: High-efficiency constant-current PWM-dimmable
  DC-DC buck converters, specialized for LEDs. One per series, driving
  a set of identical LEDs. One driver per LED board.

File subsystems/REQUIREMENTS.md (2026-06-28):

# PeaPod Subsystem Requirements Document Outlines

## Common Structure for Every Subsystem Requirements Document

Each subsystem requirements document should use the following structure.

### 1. Document Control

* Subsystem name
* Revision
* Date
* Owner
* Related system-level requirements
* Related interface-control documents
* Related verification plans

### 2. Purpose

State what the subsystem exists to do in one paragraph.

### 3. Scope

Define what is included and excluded.

Include:

* controlled variables owned by the subsystem;
* physical components included;
* software/control functions included;
* data generated by the subsystem;
* maintenance responsibilities.

Exclude:

* adjacent subsystem responsibilities;
* assumptions handled by the system-level design;
* future/optional capabilities not required for the current design.

### 4. Definitions

Define all subsystem-specific terms, units, and controlled quantities.

### 5. Parent Requirements and Traceability

List the system-level requirements, objectives, and metrics allocated to the subsystem.

Example categories:

* food production support;
* environment control;
* automation;
* reproducibility;
* safety;
* modularity;
* maintainability;
* resource efficiency.

### 6. Subsystem Overview

Describe the subsystem at a high level.

Include:

* functional description;
* major components;
* physical boundaries;
* control boundaries;
* data boundaries;
* relationship to other subsystems.

### 7. Interfaces

Define all subsystem interfaces.

Include:

* mechanical interfaces;
* electrical power interfaces;
* signal/control interfaces;
* data/logging interfaces;
* fluid interfaces;
* air/gas interfaces;
* thermal interfaces;
* user/maintenance interfaces.

### 8. Operating Modes

Define all required modes.

Typical modes:

* Off
* Startup
* Standby
* Active Control
* Calibration
* Maintenance
* Fault
* Safe Shutdown

### 9. Functional Requirements

State what the subsystem shall do.

Each requirement should be written as:

> The subsystem shall...

Each requirement should be atomic, testable, and uniquely identified.

### 10. Performance Requirements

State quantitative performance requirements.

Include:

* range;
* stability;
* response rate;
* accuracy;
* precision;
* sampling frequency;
* duty cycle;
* power consumption;
* environmental limits.

### 11. Safety Requirements

State how the subsystem prevents harm to:

* crew/operators;
* plants;
* adjacent subsystems;
* spacecraft/cabin environment;
* food output;
* dataset integrity.

### 12. Fault Detection and Failure Behavior

Define:

* detectable fault conditions;
* required alarms;
* automatic recovery behavior;
* safe-state behavior;
* degraded operating modes;
* data recorded during faults.

### 13. Data and Reproducibility Requirements

Define:

* required logged variables;
* timestamps;
* sensor identifiers;
* actuator states;
* calibration metadata;
* units;
* sampling rates;
* data export requirements.

### 14. Modularity and Maintainability Requirements

Define:

* replaceable components;
* required documentation;
* required tools;
* maximum replacement time;
* allowed/disallowed permanent modifications;
* connector/interface standardization.

### 15. Verification and Validation Matrix

For each requirement, list:

* requirement ID;
* verification method: inspection, analysis, test, demonstration;
* test condition;
* acceptance threshold;
* required evidence.

### 16. Open Issues and TBDs

Track values that are not yet known.

Examples:

* exact stability tolerance;
* final sensor model;
* acceptable noise level;
* calibration interval;
* subsystem-level power budget.

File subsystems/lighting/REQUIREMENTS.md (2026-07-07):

# Lighting Subsystem Requirements

## 1. Purpose

The lighting subsystem shall provide programmable plant-growth lighting with controlled intensity, spectrum, photoperiod, and spatial distribution suitable for reproducible phenotype dataset generation and food production.

## 2. Scope

### Included

* light sources;
* drivers;
* dimming/control electronics;
* spectral channels;
* mounting;
* optical surfaces directly part of lighting;
* light intensity sensing if allocated;
* safety interlocks if allocated;
* photoperiod execution.

### Excluded

* housing-level light sealing except interface requirements;
* plant selection;
* air thermoregulation except lighting heat output as a disturbance;
* imaging lights unless included in the growth-light system.

## 3. Parent Requirements Allocated

* lighting control;
* plant growth input provision;
* environment program execution;
* palatability/variety support;
* energy efficiency;
* reproducibility;
* process safety;
* modularity.

## 4. Key Interfaces

### Inputs

* light program;
* intensity setpoints;
* spectral channel setpoints;
* photoperiod schedule;
* power;
* thermal limits;
* door/open state if interlocked.

### Outputs

* photons to canopy;
* heat load;
* light-state telemetry;
* power consumption;
* fault states.

### Interfaces to Other Subsystems

* Automation: commands, schedules, telemetry, imaging.
* Housing: mounting, reflectivity, light isolation.
* Air Thermoregulation: heat load coordination.
* Humidification/Dehumidification: condensation protection.

## 5. Operating Modes

* LIGHT-MODE-001: Off
* LIGHT-MODE-002: Standby
* LIGHT-MODE-003: Active
* LIGHT-MODE-004: Sanitization
* LIGHT-MODE-005: Imaging
* LIGHT-MODE-006: Fault

## 6. Requirements

* LIGHT-REQ-001: MUST provide controlled light to the plant canopy.
* LIGHT-REQ-002: MUST support programmable photoperiods (on/off).
* LIGHT-REQ-003: MUST support programmable light intensity (dimming).
* LIGHT-REQ-004: MUST support programmable spectral channels.
* LIGHT-REQ-005: SHOULD report commanded and active lighting states.
* LIGHT-REQ-006: SHOULD support sanitization via disinfection light if allocated.
* LIGHT-REQ-007: SHOULD support imaging light if allocated.
* LIGHT-REQ-008: MUST expose documented swappable lighting components.
* LIGHT-REQ-009: SHOULD define its heat output or thermal load for the Air Thermoregulation Subsystem.

## 7. Criteria

* LIGHT-CRIT-001: PPFD range at canopy height;
* LIGHT-CRIT-002: spectral wavelength/channel range;
* LIGHT-CRIT-003: intensity stability;
* LIGHT-CRIT-004: spatial uniformity;
* LIGHT-CRIT-005: dimming resolution;
* LIGHT-CRIT-006: photoperiod (on/off) timing accuracy;
* LIGHT-CRIT-007: maximum power draw;
* LIGHT-CRIT-008: energy efficiency;
* LIGHT-CRIT-009: thermal output;
* LIGHT-CRIT-010: expected LED lifetime.

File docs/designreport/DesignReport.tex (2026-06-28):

\documentclass{../tex/report}
\usepackage{setspace} % Setting line spacing
\usepackage{ulem} % Underline
\usepackage{caption} % Captioning figures
\usepackage{subcaption} % Subfigures
\usepackage{geometry} % Page layout
\usepackage{multicol} % Columned pages
\usepackage{array,etoolbox}
\usepackage{fancyhdr}
\usepackage{enumitem}
\usepackage[toc,page]{appendix}
\setlist{noitemsep}

%READ THIS:
%mark comments with OpenComment or ClosedComment as you write, so we can ctrl+f as needed.

% Page layout (margins, size, line spacing)
\geometry{letterpaper, left=1in, right=1in, bottom=1in, top=1in}
\setstretch{1}

% Headers
\pagestyle{fancy}
\lhead{PeaPod - Design Report}
\rhead{PeaPod Technologies Inc.}

\begin{document}

\begin{titlepage}
    \begin{center}
        \vspace*{1.2cm}

        \textbf{\large{PeaPod - Design Report}}

        \vspace{0.5cm}

        Primary Written Deliverable for the Deep Space Food Challenge Phase 1

        \vfill
        \input{../tex/documentation/Namecard.tex}
        \vspace{1.25cm}

        Revision 1.0\\
        PeaPod Technologies Inc.\\
        July 30th, 2021

    \end{center}
\end{titlepage}

\thispagestyle{plain}

\tableofcontents
\newpage

\section{Design Abstract}
\textbf{Prompt}: \textit{Please provide a brief summary description of your proposed food production technology within a 1,500 character limit. The abstract may answer some of the following questions: What is your proposed solution? What is novel, sustainable, and innovative about your proposed solution? What types of food does your solution create? How are you minimizing inputs and maximizing food outputs?}

PeaPod is a modular, automated plant growth environment and distributed research tool. It can generate any environment for any crop, while collecting plant growth data for optimization.

The growth environment is adaptable to many plants and mission requirements. It consists of "unit cell" cubes that can be joined upwards and sideways to increase space. It is insulated with internally-reflective panels for efficiency \cite{insulation}.

PeaPod uses automated control systems to generate desired environments. These are air thermoregulation, humidity control, LED lighting, and an aeroponics system. They are automated by an onboard computer and housed in a "control module" at the top of the unit. This lets power be "multiplied" for extended PeaPods by adding more control modules in a controller-follower topology.

Plant growth cups and lighting platforms are built on modular "trays" mounted to the inside of the housing so the user can position plants and lights to accommodate any plant size.

Throughout a growth cycle, all environment parameters and growth metrics are collected. This data trains a statistical ML model to represent the plant's phenology over time in the environment. The output function can then be optimized for yield mass, nutrient concentration, flavour, resource efficiency, or any other metric.

Combining these into an accessible open-source design, PeaPod provides unrivalled versatility and reliability to food production systems both terrestrially and on long-duration space missions.

\uline{\textbf{1498 Characters} (2 under)}

\newpage

\section{Design Report}

\subsection{Description}
\label{sec:description}

\subsubsection{Part A}
\label{sec:description-a}

\textbf{Prompt}: \textit{Please provide a more fulsome description of your food production technology. Your description needs to include information about what the technology is, what it does, how it functions, and how the crew will interact with it. Be sure to also provide any descriptions of major hardware components and processes in relation to your technology.}

PeaPod is an automated plant growth environment, made of control systems and an automation/monitoring system within a modular, cubic housing. It can generate any desired environment while collecting data on plant growth and improving yields.

NOTE: For this submission, only the 4x3 unit \textbf{Standard Extended PeaPod} is in consideration. It has one control module and one of each tray (grow and lighting) per unit.

PeaPod's control systems are made of environmental controls (feedback loops with sensors) and plant inputs (set-states):
\begin{itemize}
    \item\textit{Lighting}: LEDs, from near-ultraviolet to near-infrared. Dimmable drivers for precision spectrum and intensity control. Efficient, precise emission spectrum, low heat.
    \item \textit{Aeroponics}: Reverse osmosis (RO) water is pressurized by a pump (with sensor for safety cutoff), brought to temperature, nutrient-dosed and pH-balanced by Venturi siphons with servo-actuated flow control, and forced through nozzles to generate mist. Runoff water is recycled. Water-efficient (98\% less than farming), nutrient-efficient (60\% less), no pH/nutrient "feedback" (common in reservoir-based hydroponics), increased root oxygenation \cite{aeroponics}.
    \item \textit{Air Thermoregulation}: Leaf zone air temperature is regulated by a thermoelectric heat pump. Fans blow air over heat sinks connected to either face of a Peltier tile to circulate air and dissipate heat. A Proportionate-Integral-Derivative (PID) control system is informed by temperature sensors, and controls the direction and magnitude of the heat transfer. Low complexity, high safety/reliability, easy to automate (bidirectional, precisely dimmable, PID tuning).
    \item \textit{Humidity Regulation}: Leaf zone humidity is regulated by a dead-zone bang-bang control system informed by humidity sensors.
    \begin{itemize}
        \item \textit{Humidification}: RO water is supplied to a tank with a fine mesh piezoelectric disc. A controllable driver circuit oscillates the disk, producing water vapour. Easy to automate.
        \item \textit{Dehumidification}: A dry silica gel bead cartridge is covered by servo-actuated "shutters" to control dehumidification. Fans draw humid air through a HEPA filter into the desiccant and back into the growth environment. The beads change color to indicate water saturation. The crew is then notified to swap and "recharge" in a standard oven.
    \end{itemize}
    \item \textit{Aeroponic Water Temperature}: Root zone air temperature is regulated in the same way as the leaf zone system. Exceptions include an aluminum water block (vs internal heat sink and fan) and a single temperature sensor after the block for PID feedback in a flowing system.
    \newpage
    \item \textit{Gas Composition}: Oxygen and carbon dioxide levels are managed by gas exchange. Input and output ports allow fans to draw air into and out of the system. HEPA filters remove microbes and aerosols, and servo-actuated "shutters" prevent unintended exchange. Gas concentration sensors inform a bang-bang control system for port activation.
\end{itemize}

% Food products are optimized via plant metric analysis and machine learning. Two cameras (birds-eye and horizontal) provide data from which metrics of both plant health and yield quality are extracted. These, along with data collected on the environment, train a machine learning model to be a "digital representation" of the plant, treating environment and metrics as in/outputs to a "surrogate model". As more iterations of the plant species are grown, the dataset becomes generalized across environmental inputs/programs, and new ones can be selected via "gradient ascent" to target optimization factors (i.e. yield mass, flavour, nutrient concentration, energy/water efficiency).

\uline{\textbf{2881 Characters} (119 under)}

\vspace{0.5cm}

\subsubsection{Part B}
\label{sec:description-b}

\textbf{Prompt}: \textit{Please describe the basic operations concept of the food production technology. In your response, describe assumptions required of operation. You can also include, for example, details about whether a sterile/aseptic environment is needed, if special steps are required between production cycles, or if fluids or materials must be removed or added to prime/inoculate a system.}

Once PeaPod has been assembled, the first step is manual sterilization to prevent microbial growth at high growth environment humidities. Any plant- and food-safe means may be employed (i.e. UV).

Next is the hookup of power, network, and reverse osmosis water inputs, as well as the filling of nutrient and pH adjustment solution containers.

PeaPod's operation begins at planting. Seeds are removed from vacuum-sealed storage bags and placed in neoprene foam "pucks", which are moistened for germination and placed in grow cups. The front panel is then closed, sealing the internal environment.

The desired state of the growth environment is encoded via a standardized set of "environment parameters". The specific values of each parameter for each iteration are stored in a "program". The program is set prior to the start of plant growth, and consists of a set of \textbf{actions} (e.g. set red LEDs to 63\% power) and \textbf{control targets} (e.g. hold air temperature at 22°C) as time-series instructions from the start of planting to the point of harvest (or plant death, in the case of multiple-harvest plants) corresponding to the control systems.

When activated, PeaPod's control systems begin to enact the program. PeaPod will notify crew of any required action, including refilling inputs, cleaning components, and harvesting, as well as "End-of-Program", when all inedible plant matter is disposed of. The process can then be repeated (starting at sterilization).

\uline{\textbf{1479 Characters} (21 under)}

\newpage

\subsection{Innovation}
\label{sec:innovation}

\textbf{Prompt}: \textit{This question seeks to establish an understanding of how your technology is different from other technologies that currently exist. Your description needs to be clear and well defined using simple language when detailing how your food production technology is novel, innovative and sustainable. Ensure to provide examples that will portray the novelty of your technology.}

% Intro
% Automated food growth is far from novel, with many systems already in place to provide consumers and corporations with bulk, labour-free produce at a low cost (i.e. vertical farming). 

\textbf{Control Range and Parameter Independence}

Unlike large-scale vertical farming, PeaPod’s isolation and parameter independence lets it simulate any climate. Wide LED spectrum can emit both near-infrared and near-ultraviolet light, important for creating hormonal responses and compounds in plants. Combined with insulation, humidification and dehumidification, and thermoelectric heating/cooling, PeaPod can generate extreme environments and even conditions on other planets (minus gravity and atmospheric changes). 

These parameters are independent: e.g., lighting heat is countered by thermoregulation cooling. Also, inline nutrient and pH solution injection eliminates drawbacks of reservoir use by taking less space, less solution mixing time, and avoiding a control loop of nutrients/pH (while also being more accurate). 

%These innovations allow PeaPod to grow virtually any plant. 

\textbf{Form Factor and Extendability}

The range of output environments is also possible because of the form factor of a single PeaPod unit. Warehouse-scale vertical farming cannot provide wide-spectrum control due to size---poor insulation and air circulation prohibits extreme temperatures. PeaPod solves this with a small, modular design that enables robust lighting, heating, and cooling systems at home and at scale.

Space savings are a benefit of this feature, as the output of an entire farming or hydroponics setup (requiring a flat field or warehouse) can be spread through unused space (corners, under shelves/desks, etc.) via many small PeaPod setups. This means a large yield can be had without construction, zoning, labour, or any of the other issues accompanying large farming or hydroponic setups.

\textbf{Optimization}

Existing approaches to plant optimization are simple and ineffective, relying on a \textbf{fixed/unchanging} environment parameter set and only examining \textbf{final} plant metrics. This approach is severely limited, in that it does not account for changes over time.

Instead, statistical model is used which takes into account the cumulative property of growth. By monitoring all environment and plant indicators, repeatable and controlled trials with scientific validity are able to be performed. PeaPod counters declining health/quality indicators in real time, and generates tailored programs that to maximize any metric and target further improvement.

See the preliminary calculations Appendix \ref{app:optimization} for details.

\textbf{Open-Source Design and Data}

Since PeaPod is standard and open-source, units can be had in bulk and assembled by anybody. Public contribution to the project (both in design improvement and data) increases the reliability and safety of the solution. Collected data is, ideally, committed to the public, meaning anybody with a PeaPod can run the same iteration with the same program and species to boost scientific validity, or run a different program to expand PeaPod's knowledge base.

\uline{\textbf{2958 Characters} (42 under)}

\vspace{0.5cm}

\subsection{Adherence to Constraints}
\label{sec:constraints}

\textbf{Note}: \textit{Whether in space or in a remote community on Earth, there are several constraints that your food production technology should adhere to. This question outlines key constraints below that your technology will need to address. In Phase 1, Adherence to Constraints is not meant to determine whether the Design Report itself is complete in including all the required information. This question is meant to ensure that Teams have considered the constraints, and that the food production technology design, at a minimum, falls within those constraints. In future Phases, Teams’ food production technologies will be evaluated and scored on whether or not the design stays within the constraints so that it ultimately can meet CSA’s needs and deliver value.}

\subsubsection{Outer Dimensions, Volume}
\label{sec:constraints-volume}

\textbf{Constraint}: \textit{Fits through 1.07m x 1.90m doorway; W < 1.820m, D < 2.438m, H < 2.591m; V<= 2m${}^3$}

% 300chars

% PeaPod is a modular system of "unit cells," each consisting of a .5 x .5 x .5 meter cube frame with insertable insulation panels. This cell is expandable to physically link with neighbouring cells, creating a single frame. An "expanded system" may share a single control module and have no separating wall (thus producing the same environment), or may have multiple control modules operating in either a master-slave topology (again, producing a homogenous system with no separation) or may be linked only physically (having no sharing of environment or control). The adaptability of PeaPod ensures it meets the constraints of its environment while yielding as much produce as possible.

\textbf{Standard Expanded PeaPod}: 4x3x1 units (0.5m on all sides) + control module = 2m wide x 1.7m tall x .5m deep = 1.5m${}^3$ (< 2)

With width treated as depth for the purposes of the considerations of the "room size" constraint, the Standard meets this constraint.

\uline{\textbf{270 Characters} (30 under)}

\vspace{0.5cm}

\subsubsection{Power Consumption}
\label{sec:constraints-power}

\textbf{Constraint}: \textit{Avg < 1500 W, Peak < 3000 W}

For calculations and justification, see preliminary calculations Appendix \ref{app:power}.

\textbf{Total Power Consumption}: 1,284W

\uline{\textbf{98 Characters} (202 under)}

\newpage

\subsubsection{Water Consumption}
\label{sec:constraints-water}

\textbf{Unconstrained}

For calculations and justification, see preliminary calculations Appendix \ref{app:water}.

\textit{Humidification}: CNet = \textbf{500mL initial + 50mL per hour}

\textit{Aeroponics}: CNet = \textbf{1.25L primed + 1.2L per hour}.

\uline{\textbf{171 Characters} (129 under)}

\vspace{0.5cm}

\subsubsection{Mass} 
\label{sec:constraints-mass}

\textbf{Unconstrained}

For part breakdown, calculations, and justification, see preliminary calculations Appendix \ref{app:mass}.

Total: \textbf{70kg}

\uline{\textbf{83 Characters} (217 under)}

\vspace{0.5cm}

\subsubsection{Data Connection} 
\label{sec:constraints-data}

\textbf{Unconstrained}

% \textit{Automation}: All of PeaPod's operation is automated, save for a select few setup, maintenance, and harvest tasks. This is controlled by a central computer, which uses a "program" to enact the desired environment at each point in time throughout the plant life cycle. 
\textit{Remote Control}: The program may be changed \uline{instantaneously} as an \textbf{appended instruction set} with immediate effect.
% \textit{Feedback}: The feedback sensors provide the computer with information that will influence the control it exerts. For example, if the program indicates the leaf zone temperature should be set to 22 degrees C, the computer would apply greater power to the heater if the current temperature was 18 degrees C as opposed to 21 degrees C. This forms a control loop for each parameter, relying on one of many control functions (bang-bang, PID, etc.).

\textit{Data Presentation}: Plant and environment data can be viewed with \uline{live updates and video feed}.

\uline{\textbf{206 Characters} (94 under)}

\vspace{0.5cm}

\subsubsection{Crew Time Requirement - Setup \& Maintenance}
\label{sec:constraints-crewtime} 

\textbf{Constraint}: \textit{4 hrs/week}

For calculations and justification, see preliminary calculations Appendix.

Total setup process time (2 trays per unit, 12 units, 1 CM): \textbf{17.5 hours} (\textit{one person}) or \textbf{4.5 hours} (\textit{crew of 4})

Total maintenance time per week: \textbf{1-2 hours} (depending on program)

\uline{\textbf{246 Characters} (54 under)}

\newpage

\subsubsection{Palatability of Crop Output} 
\label{sec:constraints-palatability}

\textbf{Constraint}: \textit{>= 6.0 Hedonic}

Hydroponic crops have seen commercial success \cite{commercialhydro}, suggesting that their output is of sufficient hedonic quality to be desired.

\textit{Case Study in Fresh Produce}: Acceptability of Fresh Cantaloupe Melon \cite{melon}

\begin{itemize}
    \item Appearance: 7.93/9.00
    \item Aroma: 7.77/9.00
    \item Flavor: 6.83/9.00
    \item Texture: 7.43/9.00
    \item \textbf{Overall}: 7.17/9.00 (>6.00)
\end{itemize}

\uline{\textbf{292 Characters} (8 under)}

\vspace{0.5cm}

\subsubsection{Operational Constraints} 
\label{sec:constraints-operational}

\textbf{Constraint}: \textit{Terrestrial: gravity (9.81 m/s${}^2$), ambient atmospheric pressure (101,325 Pa), ambient atmospheric temperature (22 °C), ambient atmospheric humidity (50 \%RH)}

Design operates in terrestrial conditions.

Ambient pressure: tank, bladder, and nozzle are designed to produce indicated outputs at standard air pressure
Ambient temperature and humidity: less concern, housing is sealed and insulated

\uline{\textbf{231 Characters} (69 under)}

\newpage

\subsection{Performance Criteria}

\textbf{Note}: \textit{This section seeks to understand how the proposed food production technology addresses the performance criteria of the Challenge. Describe how the food production technology addresses the following performance criteria.}

\subsubsection{Acceptability}
\label{sec:acceptability}

\textbf{Acceptability of Process}
\label{sec:acceptability-process}

\textbf{Prompt}: \textit{Describe in detail the processes and procedures of using your technology. Please also provide an assessment (using industry standards and/or existing research) that your technology processes are likely to be user friendly and acceptable to the crew.}

\textbf{Target:} \textit{The process must be something crew members could be expected to accomplish in a reasonable amount of time, on a daily basis in a small kitchen-like space after a busy workday. Teams should consider the current target for Astronauts is 1 hour per meal (30 minutes for preparation, 30 minutes for the meal itself).}

% 3000chars

\textit{Footprint}:

Due to PeaPod's modular construction, the footprint can vary. For a Standard Extended PeaPod, the footprint would be 2m x 0.5m, or about three standing refrigerators. When stowed, volume is reduced to 37\% of when assembled. Control module is packed pre-assembled.

The following estimates are for a Standard Extended PeaPod.

\textit{Setup Process}:

\begin{enumerate}
    \item Assemble housing - \textbf{2 hours}
    \item Install control module(s):
    \begin{enumerate}
        \item Hook up water, power, and network inputs - \textbf{5 min}
        \item Fill nutrient and pH adjustment solution containers - \textbf{10 min}
        \item Mount CM to housing - \textbf{5 min}
    \end{enumerate}
    \item Assemble all trays - \textbf{1 hour},
    \item For each tray, either:
    \begin{enumerate}
        \item Mount lighting boards and driver, daisy chain boards to driver, hook up power and signal to driver and CM - \textbf{10 min} per tray, \textbf{OR}
        \item Mount aeroponic nozzle mount and arm, hook up water delivery line to nozzles and CM - \textbf{10 min} per tray
    \end{enumerate}
    \item UV sterilization - \textbf{20 min}
    \item Prepare and plant seeds for desired crop output, seal growth environment - \textbf{30 min}
    \item Enable primary power supply, and power on automation system, allow to perform self-test and calibrations - \textbf{10 min}
    \item Open water input shutoff valve
    \item Input program for required environments and activate - \textbf{5 min}
\end{enumerate}

Total setup process time (Standard: 2 trays per unit, 12 units, 1 CM): \textbf{8.5 hours} (\textit{one person}) or \textbf{2.5 hours} (\textit{crew of 4})

\newpage

\textit{Food Production Cycle}:

\begin{enumerate}
    \item Environment is maintained, and environment can be observed live at a computer terminal via sensor data and camera feed
    \item Circulation fans enable automated pollination
    \item Perform maintenance, including:
    \begin{itemize}
        \item Cleaning nozzle once a month - \textbf{10 min}
        \item Swapping and recharging dehumidification cartridges when instructed - \textbf{5 min} (active time)
        \item Refilling solution containers when instructed - \textbf{5 min}
    \end{itemize}
    \item Upon End-Of-Program (EOP) notification, the gas exchange system will conduct a "full equalization flush", bringing the internal environment in equilibrium with the surroundings. Users will harvest and store food products (or prepare and consume them immediately, varying time) - \textbf{15 min}
    \item Upon End-Of-Life notification (may occur at the same time as EOP), the plant is scrapped (\textbf{15 min}), and new plants may be planted
\end{enumerate}

Total maintenance time per week: \textbf{1-2 hours} (depending on program)

\textit{Process Evaluation}:

Setup and maintenance processes are fully documented in a "User Manual", which includes both text instructions (with numerical specifications for different actions) as well as diagrams for reference. Notifications from computer refer users to specific subsections of the Manual for maintenance actions. All processes require no specific expertise, just the ability to operate basic hand tools and follow instructions.

All interactions with the automation system (i.e. program upload, environment/camera monitoring) can be accomplished either via a touchscreen panel on the front of the control module or over the Internet.

\uline{\textbf{2765 Characters} (235 under)}

\newpage

\textbf{Acceptability of Food Products}
\label{sec:acceptability-products}

\textbf{Prompt}: \textit{Please provide an assessment (using industry standards and existing research) that the food outputs of your technology are likely to meet the acceptability target. Rate and describe the potential acceptability of your food products on a 9 point hedonic scale in terms of appearance, aroma, flavor, and texture. The hedonic scale is a quantitative method that is accepted throughout the food science industry as a means to determine acceptability.}

\textbf{Target}: \textit{A food item measuring an overall acceptability rating of 6.0 or better on a 9-point hedonic scale for the duration of the mission is considered acceptable.}

% 3000chars

There are several considerations when examining the acceptability of the products of our system:

\begin{enumerate}
    \item Produce is not only eaten fresh, but also forms the basis for an innumerable variety of combined and prepared foods (i.e. fresh tomatoes vs. tomato sauce);
    \item When considering prepared derivatives of the food products, the quality of the preparation is a key factor in acceptability. As such, proper care in training and is to be taken;
    \item The products formed by the system (and their properly prepared derivatives) are not exceptional or novel. They are the same plant-based foods grown, consumed, and \textbf{accepted} terrestrially, just grown in a more efficient and controlled way. As such, their acceptability is determined to be of \textbf{equal or greater value};
    \item Plant-environment optimization can be targeted not only at nutritional value or efficiency, but also at acceptability. The feedback can be gathered either through crew Hedonic rating (i.e. tomatoes grown in environment ABC rate X in appearance, Y in aroma, etc.) or more sophisticated analysis (i.e. computer vision analysis of color/size/shape for appearance, tissue concentrations of various aroma/flavor compounds); %TODO: cite some times when this has been performed, i.e. MIT basil study
\end{enumerate}

\uline{\textbf{1330 Characters} (1670 under)}

% Optional - Additional comments
% This additional text box with a 1,000 character limit allows you to provide any other information on acceptability and palatability you would like to submit to the Judging Panel.

\newpage

\subsubsection{Safety}
\label{sec:safety}

\textbf{Note}: \textit{The overall safety of the food production process and the food products are a top priority for this Challenge. No pathogens are permitted to exist within the food technology or its outputs.  Teams must take this into account in their Phase 1 designs. Designs that fail to account for pathogens will receive a "fail" score on the Safety category.}

\textbf{Safety of Process}
\label{sec:safety-process}

\textbf{Prompt}: \textit{Your answer will need to describe the safety associated with the food production process using your technology. The food production process includes: the safety of the food handling or processing procedures and environmental safety. Please include all food safety procedures that need to be followed.}

\textbf{Targets:}
\begin{itemize}
    \item Avoidance of hazardous compounds or materials used or produced (e.g., microbes, off-gassing, toxic components);
    \item Avoidance of hazards associated with cleaning this technology prior to and/or after use;
    \item Avoidance of physical, chemical, or biological hazards associated with the hardware or the process;
    \item No pathogens (i.e. nitrogen fixing bacteria); all nutrients provided directly;
    \item Clear mitigation strategies to address the aforementioned risks;
\end{itemize}

% 3000chars

Being a sustainable isolated unit, PeaPod requires little cleaning, limited to UV sterilization each time it is opened.

PeaPod uses safe materials in its chassis, insulation and circuitry. 
The main frame is constructed using aluminum. Although large quantities of aluminum in food are deemed dangerous, the lack of direct contact exposure of aluminum to the plants passes well below the toxicity limit \cite{aluminum}.
The bracketing and mounts of PeaPod are constructed using PETG plastic which has been deemed “food-safe plastic” \cite{petg}.

The foam insulation used in PeaPod is commonly used for housing and other common safe applications. 

To avoid toxins in circuitry, lead-free soldering was used for all electronics. The dehumidification system uses silica gel, which is commonly found in food packets and is deemed “biodegradable and non-toxic” \cite{silica}.

All voltages are sub 48V DC, avoiding any high-voltage risks. The voltage risk is also mitigated by short-circuit/overcurrent protection. 
All pressures experienced by the aeroponics system stay below 100 PSI, avoiding dangers with high pressures. The dangers with pressures are also mitigated through the use of PTFE tape, fail-safe solenoids (which primarily stay closed) and a pressure sensor shutoff. 

Materials selection eliminates the risk of off-gassing. The presence of microbes or other harmful pathogens are mitigated through the use of clean seeds, reverse osmosis water and pure nutrient/pH solutions, as well as "gas exchange equilibrium" and UV sterilization pre- and post-opening. HEPA filters on both gas exchange ports and the dehumidification cartridge (which is removed from the chamber) mitigate microbial and aerosol presence. Through a nutrient injection manifold, PeaPod also has the ability to administer custom solutions, such as anti-pathogenic compounds (fungicides, algicides).
In addition, PeaPod provides plant nutrients directly without the use of nitrogen-fixing bacteria. The production process is fully automated, mitigating all risks associated with human error. 

In the event of a malfunction, PeaPod also allows the user to override the program for the purposes of editing or shutting down the unit.

\uline{\textbf{2213 Characters} (787 under)}

\vspace{0.5cm}

\textbf{Safety of Food Products}
\label{sec:safety-products}

\textbf{Prompt}: \textit{Your answer will need to describe the safety of the resulting food products (outputs), including safety for repeated human consumption.}

\textbf{Target}: \textit{Consumption safety: Resulting food product is safe for repeated human consumption as defined by NASA-STD-3001 (see Reference Materials)}

% 3000chars

PeaPod provides astronauts the ability to select and grow produce of their choosing. Before takeoff, the representatives responsible for selecting and scheduling food resources for the duration of the trip must create a stockpile of seeds that will provide ample food for the astronauts throughout their journey. The variety, quality, and acceptability of crop selection is the primary variable for repeated consumption.

By maintaining optimal growth cycles, PeaPod ensures that the food produced is clean, varied, and fresh. However, program selection (especially those with chemical components, i.e. nutrient and pH solutions) also play a role, as these directly influence the composition of the food products.

The selection of proper crops and solutions, along with proper harvesting and processing techniques (i.e. only harvesting edible bodies, cooking for long enough) and harvesting timing (mitigated by notification), are the only concerns when it comes to product safety.

\uline{\textbf{982 Characters} (2018 under)}

% Optional - Additional comments
% This additional text box with a 1,000 character limit allows you to provide any other information on the safety associated with the food production process using your technology.

\newpage

\subsubsection{Resource Inputs and Outputs}
\label{sec:resource}

\textbf{Note}: \textit{In your response, you will need to describe the resource requirements of the food production process (inputs) and all outputs. You will need to also include the estimated quantities of each input and output, as well as the nutritional quality of the food product.}

\textbf{Resource Inputs}
\label{sec:resource-inputs}

\textbf{Prompt}: \textit{Indicate the inputs needed to run your food production technology. Inputs may include: Raw materials, energy, water, or other materials that enter the system.}

% 3000chars

\textit{Infrastructural Inputs}: Reverse osmosis water (constant supply at positive pressure from onboard RODI system), nutrient solutions (stored, one container each plus refill tanks), pH solutions (one container pH up, one container pH down, plus refill tanks, stored), power (onboard power, standard 120V AC 60Hz), network connection (onboard network, for remote control, live video/data transmission), plant seeds (stored in vacuum-sealed seed bank, selected for variety and acceptability), input air (HEPA filtered, carbon dioxide-rich)

\textit{Process Inputs}: Plant species identifiers, environment program (for entire growth cycle, one per plant species), nutrient and pH-adjustment solution identifiers (compounds and molarities, i.e. solution A is 0.6M NaNO${}_3$)

Common nutrient solutions target specific ions, including bioavailable nonmetals (nitrates/nitrites, ammonia/ammonium, phosphates, sulphates), metals (potassium, calcium, magnesium, iron) and other trace elements.

\uline{\textbf{755 Characters} (2245 under)}

\vspace{0.5cm}

\textbf{System Outputs}
\label{sec:resource-outputs}

\textbf{Prompt}: \textit{Indicate the outputs generated from your food production technology. }

% 3000chars

\textit{Products}: Edible plant matter, recorded environment data, plant metric data, live video feed, time-lapse capture

\textit{Byproducts}: Inedible plant matter (stems/roots/leaves/etc., waste), sensible heat (from thermoregulation pumping, managed by onboard heating/cooling), exhaust air (via HEPA filter, sterilized and dehumidified by onboard life support, oxygen-rich), minimal water vapour (as a result of higher air humidity, minimized by housing seal), latent heat (as a result of higher leaf zone temperature, minimized by insulation)

\uline{\textbf{535 Characters} (2465 under)}

\newpage

\textbf{Optimization}
\label{sec:resource-optimization}

\textbf{Prompt}: \textit{Provide a description on how the food production technology achieves the maximum amount of food output in relation to the quantity of inputs and quantity of waste output.} 

% 1500chars

\begin{itemize}
    \item \textit{High Success Rates}: Complete automation and environmental control ensures high crop success rates and yield predictability.
    \item \textit{Repeatability}: Once optimal conditions are found for a given crop species, they can be repeated ad infinitum.
    \item \textit{Immediate Sensor Feedback and Response}: Immediate feedback from both environment sensors and plant metric analysis empowers the system to respond to unpredictable or otherwise uncontrolled factors (i.e. poor seed health, outside interference). Plant metric analysis can be used to diagnose program ineffectualities, accelerate optimization, and preventatively mitigate plant health decline.
    \item \textit{Data Collection, Yield Optimization}: By collecting data via computer vision and post-harvest yield evaluation (GCMS, weighing, etc.) on the plant's response to the induced environment, the relationship between the species behaviour and the surrounding environment can be analyzed. Plant metrics include plant health indicators (chlorophyll concentrations/chlorosis, leaf count/size distribution/density, plant height/canopy dimensions leaf tip burn, leaf curl, wilting, etc.) and crop yield (edible matter net mass/percent mass of plant, total plant mass, chemical/nutritional composition, caloric measurement, etc.). Data is filtered/smoothed across time to account for noise. The relationship is then represented by a statistical/machine learning model via a method known as "surrogate modelling". The method for this analysis can be found in the preliminary calculations Appendix \ref{app:optimization}.
    
\end{itemize}

\uline{\textbf{1479 Characters} (21 under)}

\vspace{0.5cm}

\textbf{Food Output Quality}
\label{sec:resource-outputquality}

\textbf{Prompt}: \textit{Please describe  the nutritional quality of the resulting food products from your technology. You will need to provide the nutritional potential of the food produced with your technology. Use values based on reasonable literature information that you can reference.}

\textbf{Targets:}
\begin{itemize}
    \item Maximum macronutrients supplied, as a percentage of a crewmember’s complete dietary needs;
    \item Maximum micronutrients supplied, as a percentage of a crewmember’s complete dietary needs;
    \item Maximum variety of nutrients supplied;
\end{itemize}

% 3000chars

Given the system can induce a wide and continuous range of environments, it can produce environments suitable for any aeroponically-growable crop. Within the 2 square meters allotted to the solution, 12 PeaPods can be placed in a Standard configuration, resulting in a hypothetical maximum of 4 different environments (4 vertical columns with 4 control modules). The sum of the plants grown can be any combination of any number of suitable plant species (grouped into the same environment if suitable, i.e. different microgreens together), and as such, can be selected to meet all macro and micro nutrient requirements (with fortification or supplementation of those nutrients not found in plants \cite{plantbased}).
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

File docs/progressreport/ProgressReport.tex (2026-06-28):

\documentclass{../tex/report}
\usepackage{setspace} % Setting line spacing
\usepackage{ulem} % Underline
\usepackage{caption} % Captioning figures
\usepackage{subcaption} % Subfigures
\usepackage{geometry} % Page layout
\usepackage{multicol} % Columned pages
\usepackage{array,etoolbox}
\usepackage{fancyhdr}
\usepackage{enumitem}
\usepackage[toc,page]{appendix}
\setlist{noitemsep}

% Page layout (margins, size, line spacing)
\geometry{letterpaper, left=1in, right=1in, bottom=1in, top=1in}
\setstretch{1}

% Headers
\pagestyle{fancy}
\lhead{PeaPod - Solution Overview \& Progress Report}
\rhead{PeaPod Technologies Inc.}

\begin{document}

\begin{titlepage}
    \begin{center}
        \vspace*{1.2cm}
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

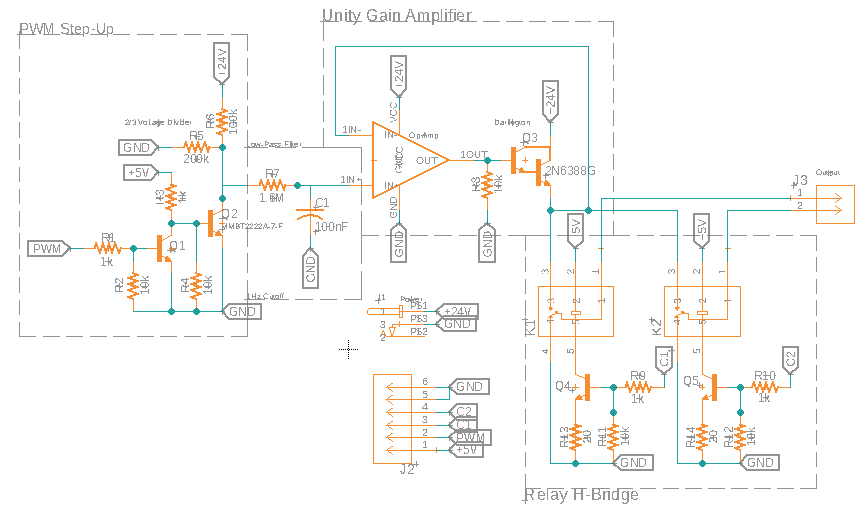
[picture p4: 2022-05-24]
docs/assets/schematics/thermoregulation_driver_sch.png

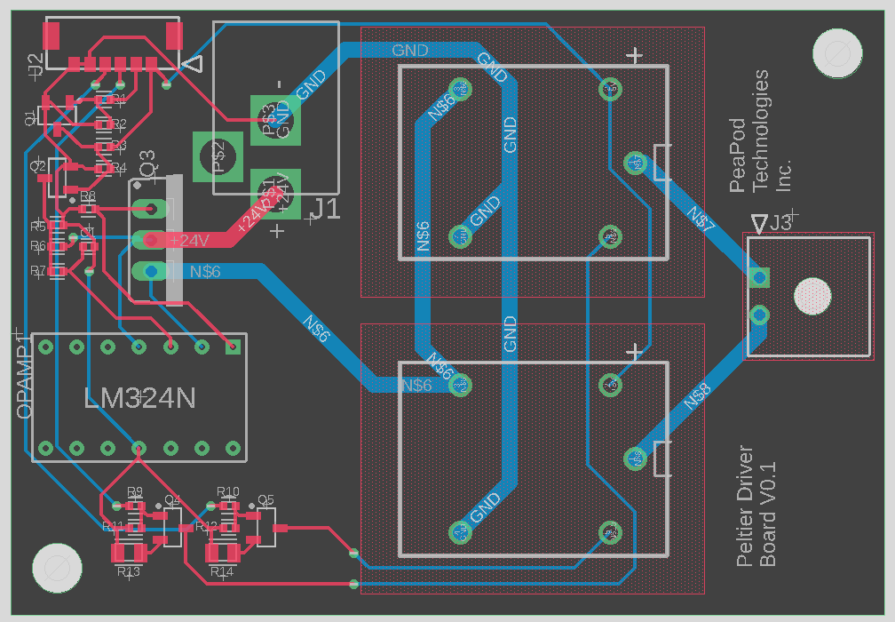
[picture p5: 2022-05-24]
docs/assets/schematics/thermoregulation_driver_brd.png

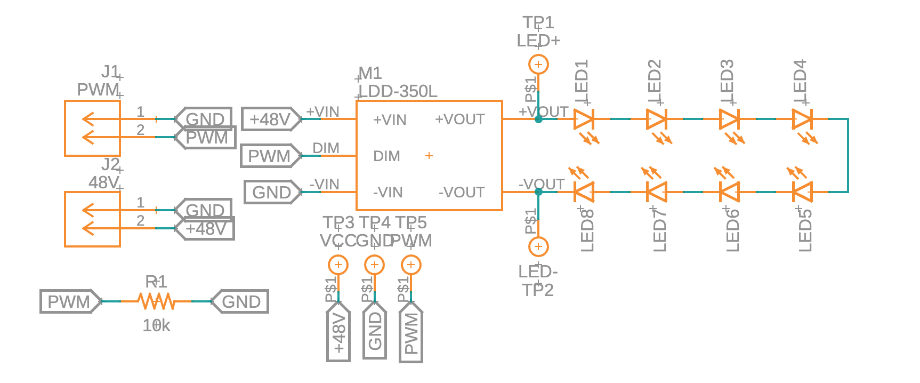
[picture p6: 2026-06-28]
subsystems/lighting/hardware/led/schematics/lighting_sch.png

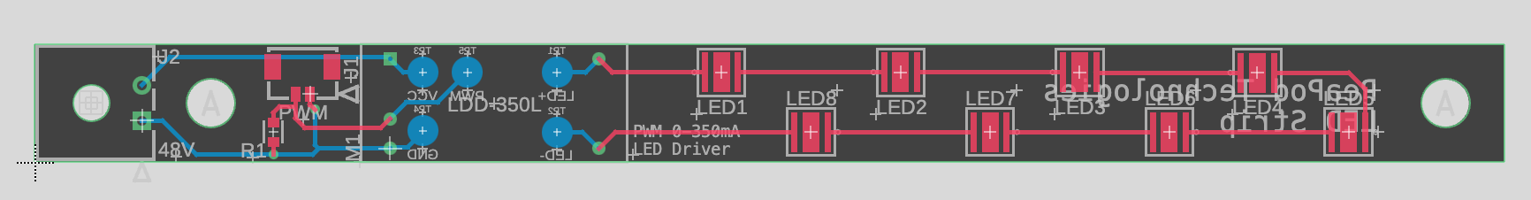
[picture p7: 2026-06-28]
subsystems/lighting/hardware/led/schematics/lighting_brd.png

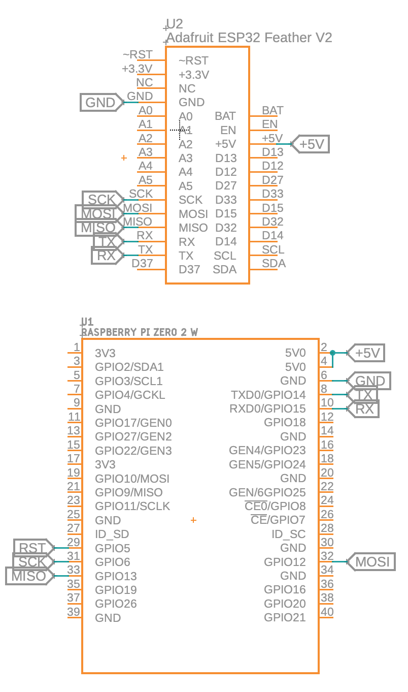
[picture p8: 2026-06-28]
subsystems/automation/hardware/schematics/automation_sch.png

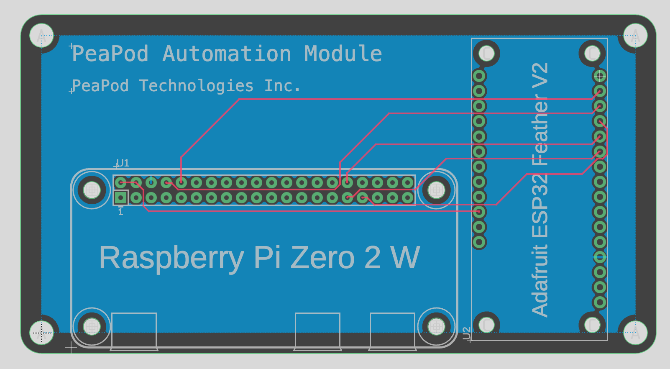
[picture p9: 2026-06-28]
subsystems/automation/hardware/schematics/automation_brd.png

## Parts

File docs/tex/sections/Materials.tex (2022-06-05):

\subsection{Materials}

As of May 31st, any false or absent entries are as a result of design and/or prototype incompleteness.

\subsubsection{System}

For a 4x3 extended topology with two control modules:
\begin{itemize}
    \item 2x Control Module, each comprises:
    \begin{itemize}
        \item 1x Automation (Tables \ref{tab:automation_parts}, \ref{tab:automation_components})
        \item 1x Aeroponics Supply (Tables \ref{tab:aeroponics_supply_components}, \ref{tab:aeroponics_supply_parts})
    \end{itemize}
    \item 12x Housing, each comprises:
    \begin{itemize}
        \item 1x Housing Shell (Tables \ref{tab:housing_shell_parts}, \ref{tab:housing_shell_fabrication})
        \item 1x Grow Tray, each with:
        \begin{itemize}
            \item 1x Grow Tray Frame (Tables \ref{tab:housing_growtray_parts}, \ref{tab:housing_growtray_fabrication})
            \item 1x Aeroponics Watering System (Tables \ref{tab:aeroponics_watering_parts})
        \end{itemize}
        \item 1x Lighting Tray (Tables \ref{tab:housing_lightingtray_parts}, \ref{tab:housing_lightingtray_fabrication})
    \end{itemize}
\end{itemize}

\clearpage

\textbf{Automation}
\begin{table}[!ht]
    \centering
    \begin{tabular}{|l|l|c|l|l|}
    \hline
        Part            & Description                       & Quantity  & Supplier  & Part Number  \\ \hline
        Motherboard PCB & 2 Layers, HASL Finish (Lead-Free) & 1         & JLCPCB    & -                     \\ \hline
    \end{tabular}
    \caption{Automation subsystem parts.}
    \label{tab:automation_parts}
\end{table}

\begin{table}[!ht]
    \centering
    \begin{tabular}{|l|l|l|c|}
    \hline
        Part Number         & Manufacturer              & Description                   & Quantity  \\ \hline
        A000005             & Arduino                   & Arduino Nano ATMega328        & 1         \\ \hline
        S404GSEJ6-U3000-3   & Delkin Devices, Inc.      & 4GB MicroSD                   & 1         \\ \hline
        61304021121         & Würth Elektronik          & Male Header Pins 40POS        & 1         \\ \hline
        SC0510              & Raspberry Pi              & Raspberry Pi Zero 2 W         & 1         \\ \hline
        DMN2005K-7          & Diodes Incorporated       & MOSFET N-CH 20V 300mA         & 2         \\ \hline
        RC0603FR-0710KL     & YAGEO                     & Res 10K Ohm 1/10W             & 5         \\ \hline
        4484                & Adafruit Industries LLC   & 1.3" TFT Screen               & 1         \\ \hline
        5055670271          & Molex                     & Molex Micro-Lock PLUS 2pos    & 2         \\ \hline
        5055670471          & Molex                     & Molex Micro-Lock PLUS 4pos    & 5         \\ \hline
        5055670871          & Molex                     & Molex Micro-Lock PLUS 8pos    & 3         \\ \hline
        5055670681          & Molex                     & Molex Micro-Lock PLUS 6pos    & 3         \\ \hline
    \end{tabular}
    \caption{Automation system electronic components.}
    \label{tab:automation_components}
\end{table}

\clearpage

\textbf{Housing}\\
\uline{Shell}
\begin{table}[!ht]
    \centering
    \begin{tabular}{|l|l|c|l|l|}
    \hline
        Part                    & Description                   & Quantity  & Supplier      & Part Number   \\ \hline
        Control Module Housing  & 5-Sided Enclosure             & 1         & Protocase     & -             \\ \hline
        Frame Front X           & 20x20mm, Cut to 500mm         & 2         & McMaster-Carr & 5537T101      \\ \hline
        Frame Door Y            & 20x20mm, Cut to 500mm         & 2         & McMaster-Carr & 5537T101      \\ \hline
        Frame Rear X            & 20x20mm, Cut to 460mm         & 2         & McMaster-Carr & 5537T101      \\ \hline
        Frame Door X            & 20x20mm, Cut to 460mm         & 2         & McMaster-Carr & 5537T101      \\ \hline
        Frame Rear Y            & 20x40mm, Cut to 460mm         & 2         & McMaster-Carr & 5537T111      \\ \hline
        Frame Front Y           & 20x20mm, Cut to 460mm         & 2         & McMaster-Carr & 5537T101      \\ \hline
        Frame Z                 & 20x20mm, Cut to 460mm         & 4         & McMaster-Carr & 5537T101      \\ \hline
        Foam Insulation         & GPS, 4' x 8' x 1"             & 1         & Home Depot    & 1001211234    \\ \hline
        Reflective Laminate     & 27" x 12' x 0.002"            & 1         & McMaster-Carr & 7538T11       \\ \hline
        Adhesive                & LePage PL300 Foamboard        & 2         & Home Depot    & 1000403469    \\ \hline
        Door Hinges             & Plastic, Black                & 2         & McMaster-Carr & 5537T85       \\ \hline
        Feet Bumpers            & Adhesive-Back                 & 4         & McMaster-Carr & 95495K24      \\ \hline
        M5x0.8 10mm Bolts       & Alloy Steel, Socket Head Cap  & 44        & McMaster-Carr & 91290A224     \\ \hline
        M5 T-Nuts               & Zinc-Plated Steel             & 44        & McMaster-Carr & 5537T651      \\ \hline
    \end{tabular}
    \caption{Housing shell parts.}
    \label{tab:housing_shell_parts}
\end{table}

\begin{table}[!ht]
    \centering
    \begin{tabular}{|l|c|l|l|}
    \hline
        Part        & Quantity  & Materials     & Process       \\ \hline
        L Bracket   & 8         & PETG Filament & 3D Printing   \\ \hline
        T Bracket   & 4         & PETG Filament & 3D Printing   \\ \hline
        Feet        & 4         & PETG Filament & 3D Printing   \\ \hline
    \end{tabular}
    \caption{Housing shell fabricated parts.}
    \label{tab:housing_shell_fabrication}
\end{table}

\clearpage

\uline{Grow Tray}
\begin{table}[!ht]
    \centering
    \begin{tabular}{|l|l|c|l|l|}
    \hline
        Part                & Description                   & Quantity  & Supplier          & Part Number   \\ \hline
        Tray X              & 20x20mm, Cut to 440mm         & 2         & McMaster-Carr     & 5537T101      \\ \hline
        Tray Z              & 20x20mm, Cut to 400mm         & 3         & McMaster-Carr     & 5537T101      \\ \hline
        Nozzle Arm          & 20x20mm, Cut to 150mm         & 2         & McMaster-Carr     & 5537T101      \\ \hline
        M5x0.8 10mm Bolts   & Alloy Steel, Socket Head Cap  & 25        & McMaster-Carr     & 91290A224     \\ \hline
        M5x0.8 16mm Bolts   & Alloy Steel, Socket Head Cap  & 20        & McMaster-Carr     & 91290A232     \\ \hline
        M4x0.7 16mm Bolts   & Alloy Steel, Socket Head Cap  & 12        & McMaster-Carr     & 91290A154     \\ \hline
        M4x0.7 Hex Nuts     & High-Strength Steel           & 12        & McMaster-Carr     & 94166A110     \\ \hline
        M5 T-Nuts           & Zinc-Plated Steel             & 35        & McMaster-Carr     & 5537T651      \\ \hline
        M5x0.8 Hex Nuts     & Alloy Steel                   & 2         & McMaster-Carr     & 94166A120     \\ \hline
        Grow Cup            & 2" Diameter                   & 16        & Amazon            & ~             \\ \hline
    \end{tabular}
    \caption{Grow tray frame parts.}
    \label{tab:housing_parts}
\end{table}

\begin{table}[!ht]
    \centering
    \begin{tabular}{|l|c|l|l|}
    \hline
        Part                    & Quantity  & Materials             & Process           \\ \hline
        L Bracket (Grow Tray)   & 4         & PETG Filament         & 3D Printing       \\ \hline
        Diagonal Bracket        & 4         & PETG Filament         & 3D Printing       \\ \hline
        T Bracket               & 4         & PETG Filament         & 3D Printing       \\ \hline
        Tray Hook BL            & 1         & PETG Filament         & 3D Printing       \\ \hline
        Tray Hook BR            & 1         & PETG Filament         & 3D Printing       \\ \hline
        Tray Hook FL            & 1         & PETG Filament         & 3D Printing       \\ \hline
        Tray Hook FR            & 1         & PETG Filament         & 3D Printing       \\ \hline
        Grow Plate Quarters     & 4         & 210x210x5mm PET Sheet & Table Saw         \\ \hline
        Grow Plate Washer       & 1         & PETG Filament         & 3D Printing       \\ \hline
        Nozzle Mount A          & 2         & PETG Filament         & 3D Printing       \\ \hline
        Nozzle Mount B          & 2         & PETG Filament         & 3D Printing       \\ \hline
    \end{tabular}
    \caption{Grow tray fabricated parts.}
    \label{tab:housing_growtray_fabrication}
\end{table}

\clearpage

\uline{Lighting Tray}
\begin{table}[!ht]
    \centering
    \begin{tabular}{|l|l|c|l|l|}
    \hline
        Part                & Description                   & Quantity  & Supplier          & Part Number   \\ \hline
        Tray X              & 20x20mm, Cut to 440mm         & 2         & McMaster-Carr     & 5537T101      \\ \hline
        Tray Z              & 20x20mm, Cut to 400mm         & 3         & McMaster-Carr     & 5537T101      \\ \hline
        M5x0.8 10mm Bolts   & Alloy Steel, Socket Head Cap  & 24        & McMaster-Carr     & 91290A224     \\ \hline
        M5x0.8 16mm Bolts   & Alloy Steel, Socket Head Cap  & 12        & McMaster-Carr     & 91290A232     \\ \hline
        M4x0.7 16mm Bolts   & Alloy Steel, Socket Head Cap  & 12        & McMaster-Carr     & 91290A154     \\ \hline
        M4x0.7 Hex Nuts     & High-Strength Steel           & 12        & McMaster-Carr     & 94166A110     \\ \hline
        M5 T-Nuts           & Zinc-Plated Steel             & 36        & McMaster-Carr     & 5537T651      \\ \hline
    \end{tabular}
    \caption{Lighting tray frame components.}
    \label{tab:housing_lightingtray_parts}
\end{table}

\begin{table}[!ht]
    \centering
    \begin{tabular}{|l|c|l|l|}
    \hline
        Part                        & Quantity  & Materials             & Process           \\ \hline
        L Bracket                   & 4         & PETG Filament         & 3D Printing       \\ \hline
        T Bracket                   & 2         & PETG Filament         & 3D Printing       \\ \hline
        Tray Hook BL                & 1         & PETG Filament         & 3D Printing       \\ \hline
        Tray Hook BR                & 1         & PETG Filament         & 3D Printing       \\ \hline
        Tray Hook FL                & 1         & PETG Filament         & 3D Printing       \\ \hline
        Tray Hook FR                & 1         & PETG Filament         & 3D Printing       \\ \hline
        Lighting LED Board Mount    & 5         & PETG Filament         & 3D Printing       \\ \hline
        Lighting Power Board Mount  & 1         & PETG Filament         & 3D Printing       \\ \hline
    \end{tabular}
    \caption{Lighting tray frame fabricated parts.}
    \label{tab:housing_lightingtray_fabrication}
\end{table}

\clearpage

\textbf{Aeroponics}

All parts are rated for over 100PSI.

\uline{Supply}
\begin{table}[!ht]
    \centering
    \begin{tabular}{|l|l|c|l|l|}
    \hline
        Part                            & Description               & Quantity  & Supplier              & Part Number   \\ \hline
        3/8" ID Tubing                  & 1/2" OD, 10', PET         & 1         & McMaster-Carr         & 1979T3        \\ \hline
        1/4" OD Tubing                  & 1/8" ID, 25', PET         & 1         & McMaster-Carr         & 1979T4        \\ \hline
        PTFE Tape                       & 1/2" x 21' Roll, White    & 1         & McMaster-Carr         & 4934A14       \\ \hline
        SAE \#6 Hose Clamp (Pack of 10) & 7/32" to 5/8", Steel      & 1         & McMaster-Carr         & 5415K11       \\ \hline
        Bonded O-Rings for 1/2 BSPP     & Nitrile Rubber and Steel  & 5         & McMaster-Carr         & 50915K816     \\ \hline
        Grip-Lock Socket to 1/2 MPT     & Zinc-Plated Steel         & 1         & McMaster-Carr         & 6539K37       \\ \hline
        Grip-Lock Plug to 1/2 MPT       & Zinc-Plated Steel         & 1         & McMaster-Carr         & 6539K67       \\ \hline
        Shutoff Valve                   & Brass, 1/2 FPT            & 2         & McMaster-Carr         & 47865K23      \\ \hline
        1/2 MPT to 3/8" Barb            & Brass                     & 1         & McMaster-Carr         & 2838N23       \\ \hline
        Diaphragm Pump                  & 4.1L/min @80PSI           & 1         & Amazon                & ~             \\ \hline
        3/8 MPT to 3/8" Barb            & Aluminum                  & 1         & McMaster-Carr         & 5357K37       \\ \hline
        1/2 FPT to 3x 3/8 FPT Manifold  & Aluminum, Heat Block      & 1         & McMaster-Carr         & 3491N13       \\ \hline
        3/8 MPT Manifold Plug           & Aluminum                  & 2         & McMaster-Carr         & 3867T364      \\ \hline
        1/2 MPT to 3/8" Barb            & Aluminum                  & 1         & McMaster-Carr         & 5357K38       \\ \hline
        3/8 MPT to 3/8" Barb            & Brass                     & 1         & McMaster-Carr         & 2838N22       \\ \hline
        3/8 FPT Elbow                   & Brass                     & 2         & McMaster-Carr         & 50785K37      \\ \hline
        3/8 MPT to 6 1/4" Push Connect  & Solution Manifold         & 2         & McMaster-Carr         & 5203K956      \\ \hline
        1/4" Push Connect Tee           & Plastic                   & 6         & McMaster-Carr         & 5111K528      \\ \hline
        1/4" Push Connect Plug          & Plastic                   & 6         & McMaster-Carr         & 5111K504      \\ \hline
        % 1/4" Push Connect Elbow         & Plastic                   & 8         & McMaster-Carr         & 5111K488      \\ \hline
        3/8 NPT Right-Angle Tee         & Brass                     & 1         & McMaster-Carr         & 50785K223     \\ \hline
        1/2 FPT to 3/8 MPT Adapter      & Brass                     & 1         & McMaster-Carr         & 50785K29      \\ \hline
        Accumulator Tank                & 0.75L                     & 1         & Amazon                & ~             \\ \hline
        1/2 FPT to 1/2 M BSPP Adapter   & Brass                     & 1         & McMaster-Carr         & 1786N138      \\ \hline
        1/2 BSPP Tee                    & Brass                     & 1         & McMaster-Carr         & 9151K272      \\ \hline
        1/2 BSPP Nipple                 & Brass                     & 1         & McMaster-Carr         & 9151K375      \\ \hline
        1/2 F BSPP to 1/2 MPT Adapter   & Brass                     & 1         & McMaster-Carr         & 50785K608     \\ \hline
        1/2 FPT to 1/4" OD Compression  & Brass                     & 1         & McMaster-Carr         & 51875K14      \\ \hline
    \end{tabular}
    \caption{Aeroponics supply parts.}
    \label{tab:aeroponics_supply_parts}
\end{table}

\begin{table}[!ht]
    \centering
    \begin{tabular}{|c|l|l|l|c|}
    \hline
        Part Number & Manufacturer                  & Description               & Quantity  \\ \hline
        SEN0257     & DFRobot                       & Water Pressure Sensor     & 1         \\ \hline
        GE-2158     & Amphenol Thermometrics        & Water Temperature Sensor  & 1         \\ \hline
        996         & Adafruit Industries LLC       & Solenoid Valve            & 1         \\ \hline
        114991171   & Seeed Technology Co., Ltd     & Water Flow Sensor         & 1         \\ \hline
    \end{tabular}
    \caption{Aeroponics supply electronic components.}
    \label{tab:aeroponics_supply_components}
\end{table}

\clearpage

\uline{Watering System}
\begin{table}[!ht]
    \centering
    \begin{tabular}{|l|l|c|l|l|}
    \hline
        Part                                    & Description           & Quantity  & Supplier              & Part Number   \\ \hline
        1/4" Compression Quick-Disconnect       & Plastic               & 2         & McMaster-Carr         & 5012K122      \\ \hline
        1/4" Push Connect 1/8 MPT Inline Tee    & Plastic and Brass     & 1         & McMaster-Carr         & 51235K147     \\ \hline
        1/4" Push Connect to 1/8 MPT Elbow      & Plastic and Brass     & 1         & McMaster-Carr         & 51235K127     \\ \hline
        1/8 FPT Straight Coupling               & Brass                 & 2         & McMaster-Carr         & 50785K91      \\ \hline
        80-Degree Full-Cone Misting Nozzle      & Brass, 1/8 MPT        & 2         & McMaster-Carr         & 3178K75       \\ \hline
        Dyneema Composite                       & 1.43oz, 0.5x1.5yd     & 3         & Ripstop by the Roll   & ~             \\ \hline
        Dyneema Pressure-Sensitive Adhesive     & 1/2" x 15'            & 3         & Ripstop by the Roll   & ~             \\ \hline
        Drawstring                              & Nylon Cord, 25'       & 1         & McMaster-Carr         & 3696T38       \\ \hline
        Drawstring Lock                         & Slide-Release         & 1         & McMaster-Carr         & 3734T4        \\ \hline
    \end{tabular}
    \caption{Grow tray watering system parts.}
    \label{tab:aeroponics_watering_parts}
\end{table}

\uline{Dosage Pump}
\begin{table}[!ht]
    \centering
    \begin{tabular}{|l|l|c|l|l|}
    \hline
        Part                & Description                       & Quantity  & Supplier      & Part Number   \\ \hline
        M4x0.7 16mm Bolts   & Alloy Steel, Socket Head Cap      & 4         & McMaster-Carr & 91290A154     \\ \hline
        M4x0.7 4mm Bolts    & 18-8 Stainless, Socket Head Cap   & 2         & McMaster-Carr & 91292A023     \\ \hline
        Nylon Washer        & Lubricated, 15mm x 28mm           & 2         & McMaster-Carr & 91545A510     \\ \hline
        Ball Bearing        & Sealed, Stainless Steel           & 3         & McMaster-Carr & 6138K65       \\ \hline
        3/16" OD Tubing     & 1/16" ID, 10', Tygon PVC          & 1         & McMaster-Carr & 6516T62       \\ \hline
    \end{tabular}
    \caption{Dosage pump parts.}
    \label{tab:aeroponics_dosagepump_parts}
\end{table}

\begin{table}[!ht]
    \centering
    \begin{tabular}{|l|c|l|l|}
    \hline
        Part                & Quantity  & Materials & Process       \\ \hline
        Pump Body Lower     & 1         & PETG      & 3D Printing   \\ \hline
        Pump Body Upper     & 1         & PETG      & 3D Printing   \\ \hline
        Pump Roller Lower   & 1         & PETG      & 3D Printing   \\ \hline
        Pump Roller Upper   & 1         & PETG      & 3D Printing   \\ \hline
    \end{tabular}
    \caption{Dosage pump fabricated parts.}
    \label{tab:aeroponics_dosagepump_fabrication}
\end{table}

\begin{table}[!ht]
    \centering
    \begin{tabular}{|c|l|l|l|c|}
    \hline
        Part Number   & Manufacturer  & Description               & Quantity  \\ \hline
        918           & Adafruit      & 12V Geared Stepper Motor  & 1         \\ \hline
    \end{tabular}
    \caption{Dosage pump electronic components.}
    \label{tab:aeroponics_dosagepump_components}
\end{table}

\clearpage

\textbf{Thermoregulation}\\
\uline{Leaf-Zone Heat Pump}\\
\textit{Incomplete}. Missing: heat sink.
\begin{table}[!ht]
    \centering
    \begin{tabular}{|l|l|l|c|}
    \hline
        Part Number         & Manufacturer              & Description                       & Quantity  \\ \hline
        CP854345H           & CUI Devices               & 77W Peltier, 8.5A                 & 1         \\ \hline
        2857                & Adafruit Industries LLC   & Humidity \& Temperature Sensor    & 2         \\ \hline
        FAD1-12025CBHW12    & Qualtek                   & 12VDC Axial Fan                   & 2         \\ \hline
    \end{tabular}
    \caption{Leaf-zone heat pump electronic components.}
    \label{tab:thermoregulation_leafzone_components}
\end{table}

\uline{Root-Zone Heat Pump}\\
\textit{Incomplete}. Missing: heat sinks.
\begin{table}[!ht]
    \centering
    \begin{tabular}{|l|l|l|c|}
    \hline
        Part Number         & Manufacturer              & Description                       & Quantity  \\ \hline
        CP854345H           & CUI Devices               & 77W Peltier, 8.5A                 & 1         \\ \hline
        FAD1-12025CBHW12    & Qualtek                   & 12VDC Axial Fan                   & 1         \\ \hline
    \end{tabular}
    \caption{Root-zone/aeroponics heat pump electronic components.}
    \label{tab:thermoregulation_rootzone_components}
\end{table}

\clearpage

\uline{Driver Board}
\begin{table}[!ht]
    \centering
    \begin{tabular}{|l|l|c|l|l|}
    \hline
        Part                        & Description                       & Quantity  & Supplier  & Part Number  \\ \hline
        Thermoelectric Driver PCB   & 2 Layers, HASL Finish (Lead-Free) & 1         & JLCPCB    & -                     \\ \hline
    \end{tabular}
    \caption{Thermoelectric driver parts.}
    \label{tab:automation_parts}
\end{table}

\begin{table}[!ht]
    \centering
    \begin{tabular}{|c|l|l|l|c|}
    \hline
        Part Number       & Manufacturer              & Description                   & Quantity  \\ \hline
        2N6388G           & onsemi                    & NPN Darlington 80V 10A        & 1         \\ \hline
        LM324N            & Texas Instruments         & OPAMP 4-circuit               & 1         \\ \hline
        0436450200        & Molex                     & Molex Micro-Fit 2pos          & 1         \\ \hline
        0436500201        & Molex                     & Molex Micro-Fit 2pos          & 1         \\ \hline
        0462355002        & Molex                     & 20-24AWG Crimp                & 2         \\ \hline
        G5LE-14 DC3       & Omron Electronics Inc     & Relay SPDT 10A 3V             & 2         \\ \hline
        MMBT2222A-7-F     & Diodes Incorporated       & NPN 40V 0.6A                  & 4         \\ \hline
        5055670681        & Molex                     & Molex Micro-Lock PLUS 6pos    & 1         \\ \hline
        KLDX-0202-A-LT    & Kycon, Inc.               & Barrel Jack                   & 1         \\ \hline
        KLDX-PA-0202-A-LT & Kycon, Inc.               & Barrel Jack                   & 1         \\ \hline
        RC0402JR-0710KL   & YAGEO                     & Res 10k Ohm 5\% 1/16W         & 5         \\ \hline
        CL05A104KA5NNNC   & Samsung Electro-Mechanics & Cap Cer 0.1uF 25V X5R         & 1         \\ \hline
        RC0402JR-071KL    & YAGEO                     & Res 1k Ohm 5\% 1/16W          & 4         \\ \hline
        RC0402FR-071M6L   & YAGEO                     & Res 1.6M Ohm 1\% 1/16W        & 1         \\ \hline
        RNCP0805FTD20R0   & Stackpole Electronics Inc & Res 20 Ohm 1\% 1/4W           & 2         \\ \hline
        RC0402FR-07100KL  & YAGEO                     & Res 100k Ohm 1\% 1/16W        & 1         \\ \hline
        RC0402FR-07200KL  & YAGEO                     & Res 200k Ohm 1\% 1/16W        & 1         \\ \hline
    \end{tabular}
    \caption{Thermoelectric driver electronic components.}
    \label{tab:airthermoregulation_driver_components}
\end{table}

\clearpage

\textbf{Humidification}\\
\textit{Incomplete}. Missing: Humidification driver PCB, driver components, piezoelectric mesh nebulizer disc, water tank.

\textbf{Dehumidification}\\
\textit{Incomplete}. Missing: Housing parts, shutters and servos, cartridge parts.
\begin{table}[!ht]
    \centering
    \begin{tabular}{|l|l|l|c|}
    \hline
        Part Number         & Manufacturer              & Description       & Quantity  \\ \hline
        FAD1-12025CBHW12    & Qualtek                   & 12VDC Axial Fan   & 2         \\ \hline
        1334                & Adafruit Industries LLC   & Color Sensor      & 1         \\ \hline
    \end{tabular}
    \caption{Dehumidification electronic components.}
    \label{tab:dehumidification_components}
\end{table}

\begin{table}[!ht]
    \centering
    \begin{tabular}{|l|l|c|l|l|}
    \hline
        Part                    & Description                           & Quantity  & Supplier      & Part Number   \\ \hline
        Indicating Desiccant    & Silica Gel, 6\%, Blue to Pink, 1lb    & 1         & McMaster-Carr & 2181K93       \\ \hline
        Air Filter              & PET, MERV 13, 0.3 micron, 10" x 10"   & 2         & McMaster-Carr & 3881T101      \\ \hline
    \end{tabular}
    \caption{Dehumidification parts.}
    \label{tab:dehumidification_parts}
\end{table}

\textbf{Gas Composition Regulation and Exchange}\\
\textit{Incomplete}. Missing: Housing parts, shutters and servos.
\begin{table}[!ht]
    \centering
    \begin{tabular}{|l|l|l|c|}
    \hline
        Part Number         & Manufacturer              & Description                       & Quantity  \\ \hline
        FAD1-12025CBHW12    & Qualtek                   & 12VDC Axial Fan                   & 2         \\ \hline
    \end{tabular}
    \caption{Gas exchange electronic components.}
    \label{tab:gas_components}
\end{table}

\begin{table}[!ht]
    \centering
    \begin{tabular}{|l|l|c|l|l|}
    \hline
        Part        & Description                           & Quantity  & Supplier      & Part Number   \\ \hline
        Air Filter  & PET, MERV 13, 0.3 micron, 10" x 10"   & 2         & McMaster-Carr & 3881T101      \\ \hline
    \end{tabular}
    \caption{Gas exchange parts.}
    \label{tab:gas_parts}
\end{table}

\clearpage

\textbf{Lighting}
\begin{table}[!ht]
    \centering
    \begin{tabular}{|l|l|l|c|}
    \hline
        Part Number & Name  & Description                       & Quantity  \\ \hline
        0451110600  & Molex & MicroLock PLUS Cable 6pos 50mm    & 2         \\ \hline
        0451110605  & Molex & MicroLock PLUS Cable 6pos 450mm   & 4         \\ \hline
    \end{tabular}
    \caption{Lighting subsystem cables.}
    \label{tab:lighting_components}
\end{table}

\begin{table}[!ht]
    \centering
    \begin{tabular}{|l|l|c|l|l|}
    \hline
        Part                & Description                           & Quantity  & Supplier  & Part Number   \\ \hline
        Lighting LED PCB    & 2 Layers, HASL Finish (Lead-Free)"    & 5         & JLCPCB    & -             \\ \hline
        Lighting Driver PCB & 2 Layers, HASL Finish (Lead-Free)"    & 1         & JLCPCB    & -             \\ \hline
    \end{tabular}
    \caption{Lighting subsystem PCBs.}
    \label{tab:lighting_parts}
\end{table}

\uline{Driver Board}
\begin{table}[!ht]
    \centering
    \begin{tabular}{|l|l|l|c|}
    \hline
        Part Number         & Manufacturer          & Description                           & Quantity  \\ \hline
        LDD-500HS           & MEAN WELL USA Inc.    & 0-500mA Constant-Current LED Driver   & 5         \\ \hline
        5055670681          & Molex                 & Micro-Lock PLUS 6pos                  & 3         \\ \hline
        KLDX-PA-0202-A-LT   & "Kycon, Inc."         & Barrel Plug                           & 1         \\ \hline
        KLDX-0202-A-LT      & "Kycon, Inc."         & Barrel Jack                           & 1         \\ \hline
        RC0402JR-0710KL     & YAGEO                 & Res 10k Ohm 1/16W                     & 5         \\ \hline
    \end{tabular}
    \caption{LED driver electronic components.}
    \label{tab:lighting_driver_components}
\end{table}

\uline{LED Board}\\
\textit{Incomplete}. Missing: UV LEDs.
\begin{table}[!ht]
    \centering
    \begin{tabular}{|l|l|l|c|}
    \hline
        Part Number             & Manufacturer  & Description                   & Quantity  \\ \hline
        XPGDRY-L1-0000-00501    & CreeLED, Inc. & Royal Blue LED (451nm)        & 3         \\ \hline
        XPGDWT-01-0000-00ME2    & CreeLED, Inc. & Cool White LED (5700K)        & 3         \\ \hline
        XPGDWT-H1-0000-00GE8    & CreeLED, Inc. & Warm White LED (2700K)        & 3         \\ \hline
        XPGDPR-L1-0000-00F01    & CreeLED, Inc. & Photo Red LED (645nm)         & 3         \\ \hline
        XPEBFR-L1-0000-00701    & CreeLED, Inc. & Infrared LED (730nm)          & 3         \\ \hline
        5055670681              & Molex         & Molex Micro-Lock PLUS 6pos    & 2         \\ \hline
    \end{tabular}
    \caption{LED board electronic components.}
    \label{tab:lighting_led_components}
\end{table}

\clearpage

\subsubsection{Inputs}
% Supply inputs (water, power, network), consumable inputs (pH/nutrient solutions, dehumidification cartridge)

\textbf{Supply Inputs}
\begin{itemize}
    \item \textit{Water}: reverse-osmosis, ambient
    \item \textit{Power}: 120V 60Hz AC\footnote{The power supply can be altered to suit a variety of power inputs (i.e. DC)}
    \item \textit{Network}: ethernet or wireless, optional
    \item \textit{Air Intake}: cabin air, filtered
\end{itemize}

\textbf{Consumable Inputs}
\begin{itemize}
    \item \textit{Nutrient/pH Adjusment Solutions}: powder form, vacuum-sealed pouches, specific compound makeup is variable to suit mission requirements
    \item \textit{Desiccant Cartridge}: recharged
    \item \textit{Seeds}: cleaned and disinfected, vacuum-sealed
\end{itemize}

\subsubsection{Outputs}
% Food outputs(?), by-products/waste (waste water from flushing, dehumidification cartridge)

\textbf{Food Outputs}\\
All food outputs are plant matter (leaves, fruits, roots, seeds, etc. dependent on species/preparation method). Species selection is variable to suit mission requirements.

\textbf{By-Products \& Waste}
\begin{itemize}
    \item \textit{Air Exhaust}: filtered, vented to onboard dehumidification and recirculation
    \item \textit{Seeds/Clones}: harvested, cleaned, and stored for replanting
    \item \textit{Inedible Plant Matter}: disposed of
\end{itemize}

\subsubsection{Maintenance}

\textbf{Spare Components}\\
Spares for each component (parts, fabricated parts, assembled PCBs) should be included.
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

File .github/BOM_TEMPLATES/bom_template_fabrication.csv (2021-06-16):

Part | Quantity | Materials | Materials Unit Cost (CAD) | Process | Time (min) | Reference
E.g. L Bracket A | 8 | PETG | 1.23 | 3D Printing | 47 | /hardware/frame/brackets/LBracket.step

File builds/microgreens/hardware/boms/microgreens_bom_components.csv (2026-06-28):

Index | Manufacturer Part Number | Manufacturer Name | Description | Quantity | Digi-Key Part Number | Unit Price | Extended Price | Datasheet | Reference Designator
1 | A000005 | Arduino | ARDUINO NANO ATMEGA328 EVAL BRD | 1 | 1050-1001-ND | 28.63000 | $28.63 | https://media.digikey.com/pdf/Data%20Sheets/Arduino%20PDFs/A000005.pdf | U2
2 | S404GSEJ6-U3000-3 | Delkin Devices, Inc. | 4GB MLC MICROSD CARD (-25C - +85 | 1 | 3247-S404GSEJ6-U3000-3-ND | 19.33000 | $19.33 | https://www.delkin.com/wp-content/uploads/2021/01/microSD-Industrial-Spec-Sheet-Jan-2021.pdf
3 | 61304021121 | Würth Elektronik | CONN HEADER VERT 40POS 2.54MM | 1 | 732-5310-ND | 2.70000 | $2.70 | https://www.we-online.com/katalog/datasheet/6130xx21121.pdf | U1, U2
4 | SC0510 | Raspberry Pi | ZERO 2 W | 1 |  |  |  | https://datasheets.raspberrypi.com/rpizero2/raspberry-pi-zero-2-w-product-brief.pdf | U1
5 | DMN2005K-7 | Diodes Incorporated | MOSFET N-CH 20V 300MA SOT23-3 | 2 | DMN2005K-7DICT-ND | 0.58000 | $1.16 | https://www.diodes.com/assets/Datasheets/ds30734.pdf | Q1, Q2
6 | RC0603FR-0710KL | YAGEO | RES 10K OHM 1% 1/10W 0603 | 5 | 311-10.0KHRCT-ND | 0.15000 | $0.75 | https://www.yageo.com/upload/media/product/productsearch/datasheet/rchip/PYu-RC_Group_51_RoHS_L_11.pdf | R1-5
7 | 4484 | Adafruit Industries LLC | MINI PITFT 1.3 FOR RASPBERRY PI | 1 | 1528-4484-ND | 22.02000 | $22.02 | https://media.digikey.com/pdf/Data%20Sheets/Adafruit%20PDFs/4484_Web.pdf
8 | 5055670271 | Molex | CONN HEADER SMD R/A 2POS 1.25MM | 2 | WM17038CT-ND | 1.19000 | $2.38 | https://www.molex.com/pdm_docs/ps/5055650000-000.pdf | J3, J8
9 | 5055670471 | Molex | CONN HEADER SMD R/A 4POS 1.25MM | 5 | WM17040CT-ND | 1.30000 | $6.50 | http://www.literature.molex.com/SQLImages/kelmscott/Molex/PDF_Images/987651-4888.pdf | J1, J2, J6, J9, J10
10 | 5055670871 | Molex | CONN HEADER SMD R/A 8POS 1.25MM | 3 | WM17115CT-ND | 1.77000 | $5.31 | https://www.molex.com/pdm_docs/pk/5055679200-200.pdf | J4, J5, J7
11 | 5055670681 | Molex | CONN HEADER SMD R/A 6POS 1.25MM | 3 | WM22471CT-ND | 1.42000 | $4.26 | https://www.molex.com/pdm_docs/ps/5055650002-000.pdf | J11-13

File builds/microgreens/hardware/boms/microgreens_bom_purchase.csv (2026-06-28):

Part | Description | Quantity | Supplier | Supplier Part Number | Unit Cost (CAD) | Reference
Tray Frame X
Tray Frame Y
Tray Frame Z
Tray Drawer Slide | 24in.; Pair | 1 | McMaster-Carr | 11435A28 | 42.92 | .
Tray Mesh Medium | 2ft. Wide | 1 | McMaster-Carr | 9218T13 | 119.04 | .
Tray Mesh Velcro | 1n. Wide; 30ft. Roll | 1 | McMaster-Carr | 95005K817 | 55.27 | .
Root-Zone Container Composite | 1.43oz Dyneema; 0.5yd sections; Cut & Folded | 2 | Ripstop by the Roll |  | 34.09 | .
Root-Zone Container Adhesive | Pressure-Sensitive Adhesive Tape for Dyneema; 1/2in. Wide; 5yd. Roll | 3 | Ripstop by the Roll |  | 6.41 | https://ripstopbytheroll.com/products/dyneema-composite-fabric-double-sided-adhesive-tape
Root-Zone Container Drawstring | Nylon Cord; 5/32in. dia.; 50ft. Length | 1 | McMaster-Carr | 3696T38 | 2.82 | https://www.mcmaster.com/3696T38/
Root-Zone Container Lock | Slide-to-Release Wheel; Pack of 25 | 1 | McMaster-Carr | 3734T4 | 29.23 | https://www.mcmaster.com/3734T4
Aeroponic Misting Nozzle | 80deg Full-Cone; Brass; 5gal. per hr. @100PSI; 1/8 MPT | 4 | McMaster-Carr | 3178K75 | 22.66 | https://www.mcmaster.com/3178K75/

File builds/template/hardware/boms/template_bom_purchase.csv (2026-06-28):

Part | Description | Quantity | Supplier | Supplier Part Number | Unit Cost (CAD) | Reference
Automation Motherboard PCB | 2 Layers, 1 oz. Copper, 1.6mm Thickness, Suggested: HASL Finish, White PCB, Black Silkscreen | 1 (MOQ 5) | JLCPCB | N/A | 0.51 | ../gerber/

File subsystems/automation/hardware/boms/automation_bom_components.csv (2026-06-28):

Index | Manufacturer Part Number | Manufacturer Name | Description | Requested Quantity 1 | Pack Quantity 1 | Pack Type 1 | Digi-Key Part Number 1 | Unit Price 1 | Extended Price 1 | Minimum Order Quantity 1 | Datasheet | Reference Designator | Product Notes
1 | 61304021121 | Würth Elektronik | CONN HEADER VERT 40POS 2.54MM | 1 | 1 | Bag | 732-5310-ND | 2.79000 | $2.79 | 1 | https://www.we-online.com/catalog/datasheet/61304021121.pdf | U1
2 | 1294 | Adafruit Industries LLC | MEMORY CARD SDHC 8GB CLASS 4 | 1 | 1 | Bulk | 1528-1294-ND | 39.49000 | $39.49 | 1
3 | SC1176 | Raspberry Pi | SBC 1.0GHZ 4 CORE 512MB RAM | 1 | 1 | Bulk | 2648-SC1176-ND | 21.94000 | $21.94 | 1 | https://datasheets.raspberrypi.com/rpizero2/raspberry-pi-zero-2-w-product-brief.pdf | U1
4 | 742-10010-00300 | CNC Tech | CBL HDMI-A M TO HDMI-C M 3M SHLD | 1 | 1 | Box | 1175-1676-ND | 29.00000 | $29.00 | 1 | https://www.cnctech.us/pdfs/742-10010-00300.pdf
5 | 5400 | Adafruit Industries LLC | ESP32 FEATHER V2 STEMMA QT | 1 | 1 | Bulk | 1528-5400-ND | 31.11000 | $31.11 | 1 |  | U2
6 | 61301611121 | Würth Elektronik | CONN HEADER VERT 16POS 2.54MM | 1 | 1 | Bag | 732-5327-ND | 1.33000 | $1.33 | 1 | https://www.we-online.com/components/products/datasheet/61301611121.pdf | U2
7 | 61301211121 | Würth Elektronik | CONN HEADER VERT 12POS 2.54MM | 1 | 1 | Bag | 732-5323-ND | 0.79000 | $0.79 | 1 | https://www.we-online.com/components/products/datasheet/61301211121.pdf | U2
8 | 2185 | Adafruit Industries LLC | CABLE A PLUG TO MCR B PLUG 6.56' | 1 | 1 | Bulk | 1528-2185AD-ND | 7.72000 | $7.72 | 1
9 | 2992 | Adafruit Industries LLC | OTG MICRO-USB AND ETHERNET HUB | 1 | 1 | Bulk | 1528-1615-ND | 21.87000 | $21.87 | 1 | https://mm.digikey.com/Volume0/opasdata/d220001/medias/docus/903/2992_Web.pdf
10 | 1994 | Adafruit Industries LLC | 5V 2A SWITCHING POWER SUPPLY W/ | 1 | 1 | Bulk | 1528-1994-ND | 13.38000 | $13.38 | 1
11 | 922 | Adafruit Industries LLC | BLACK USB KEYBOARD | 1 | 1 | Bulk | 1528-922-ND | 73.06000 | $73.06 | 1

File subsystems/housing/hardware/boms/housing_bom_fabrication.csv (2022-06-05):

Part | Quantity | Materials | Unit Cost (CAD) | Process | Time Each (min) | Reference
L Bracket | 12 | PETG Filament | TBA | 3D Printing | TBA | ../fabrication/brackets/bracket_l.stl
L Bracket (Grow Tray) | 4 | PETG Filament | TBA | 3D Printing | TBA | ../fabrication/brackets/bracket_l_alt.stl
Diagonal Bracket | 4 | PETG Filament | TBA | 3D Printing | TBA | ../fabrication/brackets/bracket_diagonal.stl
T Bracket | 10 | PETG Filament | TBA | 3D Printing | TBA | ../fabrication/brackets/bracket_t.stl
Tray Hook BL | 2 | PETG Filament | TBA | 3D Printing | TBA | ../fabrication/trayhook_backleft.stl
Tray Hook BR | 2 | PETG Filament | TBA | 3D Printing | TBA | ../fabrication/trayhook_backright.stl
Tray Hook FL | 2 | PETG Filament | TBA | 3D Printing | TBA | ../fabrication/trayhook_frontleft.stl
Tray Hook FR | 2 | PETG Filament | TBA | 3D Printing | TBA | ../fabrication/trayhook_frontleft.stl
Grow Plate Quarters | 4 | 210x210x5mm PET Sheet | TBA | CNC/Vinyl Cutting | TBA | ../fabrication/growtray/growtray_plate_quarter.stl
Grow Plate Washer | 1 | PETG Filament | TBA | 3D Printing | TBA | ../fabrication/growtray/growtray_plate_washer.stl
Nozzle Mount A | 2 | PETG Filament | TBA | 3D Printing | TBA | ../fabrication/growtray/growtray_nozzlemount_a.stl
Nozzle Mount B | 2 | PETG Filament | TBA | 3D Printing | TBA | ../fabrication/growtray/growtray_nozzlemount_b.stl
Lighting LED Board Mount | 5 | PETG Filament | TBA | 3D Printing | TBA | ../fabrication/lightingtray/lighting_driver_mount.stl
Lighting Power Board Mount | 1 | PETG Filament | TBA | 3D Printing | TBA | ../fabrication/lightingtray/lighting_led_mount.stl
Feet | 4 | PETG Filament | TBA | 3D Printing | TBA | ../fabrication/feet.stl

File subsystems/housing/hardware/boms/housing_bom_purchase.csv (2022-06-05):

Part | Description | Quantity | Supplier | Supplier Part Number | Unit Cost (CAD) | Reference
Control Module Housing | 5-Sided Enclosure, 16-guage 316 Stainless Steel Sheet, Powder-Coated | 1 | Protocase (www.protocase.com) |  | TBD | ../fabrication/controlmodule_enclosure.pda
Frame Front X Extrusion | Silver Painted, 20x20mm, Ordered 2ft., Cut to 500mm | 2 | McMaster-Carr | 5537T101 | 8.44 | https://www.mcmaster.com/5537T101
Frame Door Y Extrusion | Silver Painted, 20x20mm, Ordered 2ft., Cut to 500mm | 2 | McMaster-Carr | 5537T101 | 8.44 | https://www.mcmaster.com/5537T101
Frame Rear X Extrusion | Silver Painted, 20x20mm, Ordered 2ft., Cut to 460mm | 2 | McMaster-Carr | 5537T101 | 8.44 | https://www.mcmaster.com/5537T101
Frame Door X Extrusion | Silver Painted, 20x20mm, Ordered 2ft., Cut to 460mm | 2 | McMaster-Carr | 5537T101 | 8.44 | https://www.mcmaster.com/5537T101
Frame Rear Y Extrusion | Silver Painted, 20x40mm, Ordered 2ft., Cut to 460mm | 2 | McMaster-Carr | 5537T111 | 12.16 | https://www.mcmaster.com/5537T111
Frame Front Y | Silver Painted, 20x20mm, Ordered 2ft., Cut to 460mm | 2 | McMaster-Carr | 5537T101 | 8.44 | https://www.mcmaster.com/5537T101
Frame Z | Silver Painted, 20x20mm, Ordered 2ft., Cut to 460mm | 4 | McMaster-Carr | 5537T101 | 8.44 | https://www.mcmaster.com/5537T101
Tray X Extrusion | Silver Painted, 20x20mm, Ordered 2ft., Cut to 440mm | 4 | McMaster-Carr | 5537T101 | 8.44 | https://www.mcmaster.com/5537T101
Tray Z Extrusion | Silver Painted, 20x20mm, Ordered 2ft., Cut to 400mm | 6 | McMaster-Carr | 5537T101 | 8.44 | https://www.mcmaster.com/5537T101
Nozzle Arm Extrusion | Silver Painted, 20x20mm, Ordered 1ft., Cut to 150mm | 2 | McMaster-Carr | 5537T101 | 8.44 | https://www.mcmaster.com/5537T101
M5x0.8 10mm Bolts | Alloy Steel, Black Oxide Coated, Socket Head Cap | 139 (2 packs of 100) | McMaster-Carr | 91290A224 | 12.14 (0.12 ea.) | https://www.mcmaster.com/91290A224
M5x0.8 16mm Bolts | Alloy Steel, Black Oxide Coated, Socket Head Cap | 10 (1 pack of 100) | McMaster-Carr | 91290A232 | 14.72 (0.15 ea.) | https://www.mcmaster.com/91290A232/
M4x0.7 16mm Bolts | Alloy Steel, Black Oxide Coated, Socket Head Cap | 12 (1 pack of 100) | McMaster-Carr | 91290A154 | 11.71 (0.12 ea.) | https://www.mcmaster.com/91290A154/
M4x0.7 Hex Nuts | High-Strength Steel, Black Oxide Coated | 12 (1 pack of 100) | McMaster-Carr | 94166A110 | 8.30 (0.08 ea.) | https://www.mcmaster.com/94166A110/
M5 T-Nuts | Zinc-Plated Steel, Black Painted, for 5mm Slot | 139 (13 packs of 10) | McMaster-Carr | 5537T651 | 4.25 (0.43 ea.) | https://www.mcmaster.com/5537T651
M5x0.8 Hex Nuts | Alloy Steel, Black Oxide Coated | 10 (1 pack of 50) | McMaster-Carr | 94166A120 | 5.23 (0.10 ea.) | https://www.mcmaster.com/94166A120/
Foam Insulation | DUROSPAN GPS R5 4ft. x 8ft. x 1in. | 1 | Home Depot (Ca) | 1001211234 | 23.77 | https://www.homedepot.ca/product/durospan-gps-r5-4-ft-x-8-ft-x-1-06-inch-graphite-enhanced-expandable-polystyrene-insulation-board/1001211234
Reflective Laminate | 27in. x 12ft. x 0.002in., Aluminum-coated PET | 1 | McMaster-Carr | 7538T11 | 13.37 | https://www.amazon.ca/VIVOSUN-Horticulture-Highly-Reflective-Mylar/dp/B018VI75CS/
Adhesive | LePage PL300 Foamboard 295mL | 2 | Home Depot (Ca) | 1000403469 | 5.97 | https://www.homedepot.ca/product/lepage-lepage-pl-300-foamboard-adhesive-295-ml/1000403469
Grow Cup | 2in. Diameter | 16 | Amazon |  | 0.25 | https://www.amazon.ca/100-Pack-Garden-Slotted-Labels-Hydroponics/dp/B07CVFWSJ4/
Door Hinges | Plastic, Black, for 20x20mm Extrusion | 2 | McMaster-Carr | 5537T85 | 5.14 | https://www.mcmaster.com/5537T85/
Feet Bumpers | Adhesive-Back, Tapered Square Shape, Medium-Hard Polyurethane, Black | 4 (1 pack of 50) | McMaster-Carr | 95495K24 | 6.34 | https://www.mcmaster.com/95495K24

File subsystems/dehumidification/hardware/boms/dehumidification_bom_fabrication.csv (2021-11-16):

Part | Quantity | Materials | Materials Unit Cost (CAD) | Process | Time (min) | Reference
Cartridge | 1 | PETG | TBA | 3D Printing | TBA | ../fabrication/Cartridge.stl
Cartridge Lid | 1 | PETG | TBA | 3D Printing | TBA | ../fabrication/CartridgeLid.stl
Housing | 1 | PETG | TBA | 3D Printing | TBA | ../fabrication/Housing.stl

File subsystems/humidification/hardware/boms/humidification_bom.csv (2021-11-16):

Manufacturer Part Number | Manufacturer | Digi-Key Part Number | Customer Reference | Quantity | Unit Price | Extended Price | Description
C322C104K5R5TA | KEMET | 399-4329-ND | C1, C2, C5 | 3 | 0.32000 | $0.96 | CAP CER 0.1UF 50V X7R RADIAL
K103K10X7RF5UH5 | Vishay Beyschlag/Draloric/BC Components | BC2662CT-ND | C4 | 1 | 0.24000 | $0.24 | CAP CER 10000PF 50V X7R RADIAL
FG14X7R1A106KRT06 | TDK Corporation | 445-173132-1-ND | C3 | 1 | 0.75000 | $0.75 | CAP CER 10UF 10V X7R RADIAL
PV36Y502C01B00 | Bourns Inc. | 490-2926-ND | RP1 | 1 | 2.14000 | $2.14 | TRIMMER 5K OHM 0.5W PC PIN TOP
SE555P | Texas Instruments | 296-9684-5-ND | U1 | 1 | 0.64000 | $0.64 | IC OSC SINGLE TIMER 100KHZ 8-DIP
RLB0914-331KL | Bourns Inc. | RLB0914-331KL-ND | L1 | 1 | 0.66000 | $0.66 | FIXED IND 330UH 740MA 760MOHM TH
IRLZ44PBF | Vishay Siliconix | IRLZ44PBF-ND | Q1 | 1 | 3.50000 | $3.50 | MOSFET N-CH 60V 50A TO220AB
RNMF14FTC100R | Stackpole Electronics Inc | S100CACT-ND | R2 | 1 | 0.13000 | $0.13 | RES 100 OHM 1/4W 1% AXIAL
RNMF14FTC10K0 | Stackpole Electronics Inc | S10KCACT-ND | R1 | 1 | 0.13000 | $0.13 | RES 10K OHM 1/4W 1% AXIAL

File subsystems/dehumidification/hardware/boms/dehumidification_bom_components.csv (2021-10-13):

Manufacturer Part Number | Manufacturer Name | Description | Quantity | Digi-Key Part Number | Unit Price | Extended Price
1334 | Adafruit Industries LLC | RGB COLOR SENSOR WITH IR FILTER | 1 | 1528-1378-ND | 10.94000 | 10.94
FAD1-12025CBHW12 | Qualtek | FAN AXIAL 120X25.5MM 12VDC WIRE | 2 | Q638-ND | 17.28000 | 34.56

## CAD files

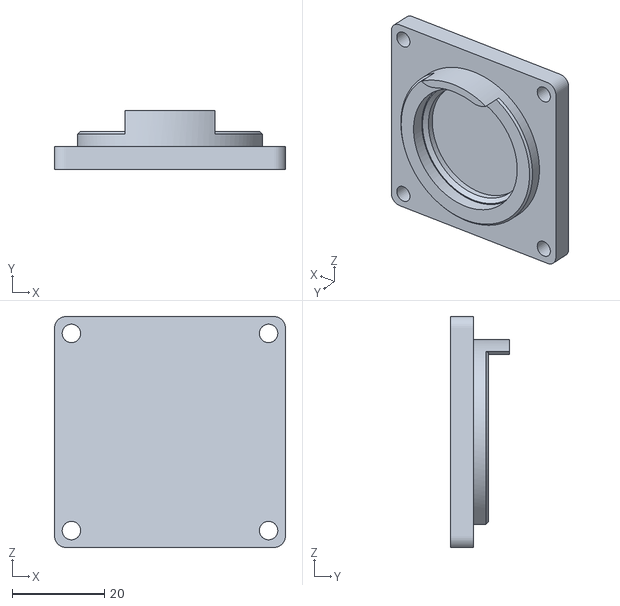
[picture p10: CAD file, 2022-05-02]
subsystems/aeroponics/hardware/dosagepump/fabrication/dosagepump_body_lower.stl
50.0 x 12.8 x 50.0

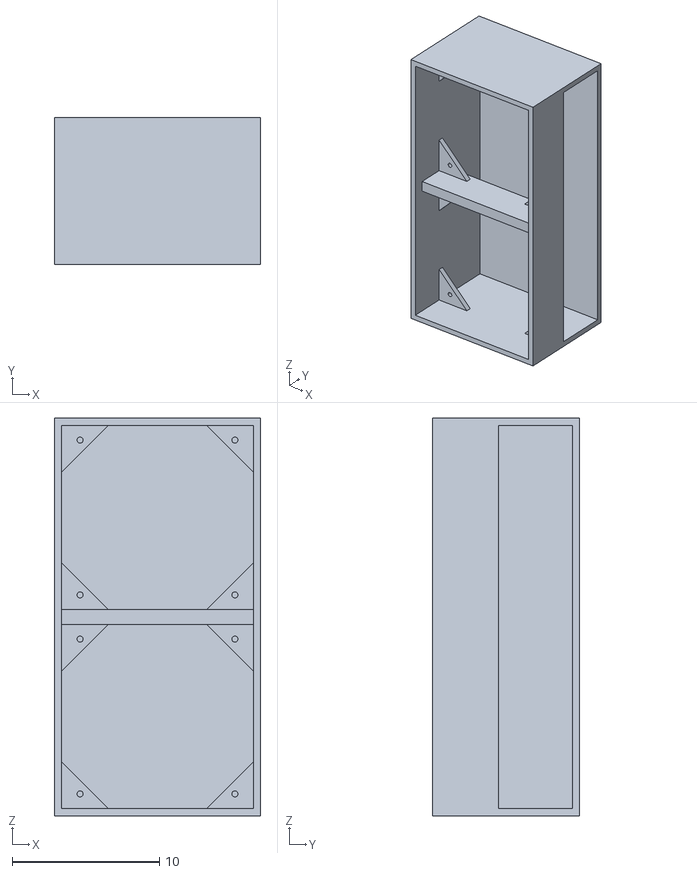
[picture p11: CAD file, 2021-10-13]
subsystems/dehumidification/hardware/fabrication/Housing.stl
14.0 x 10.0 x 27.0

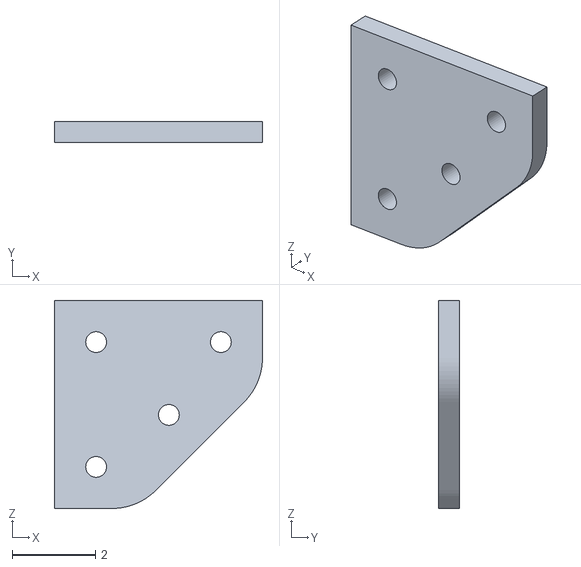
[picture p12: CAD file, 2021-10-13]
subsystems/housing/hardware/fabrication/brackets/bracket_l_alt.stl
5.00 x 0.5 x 5.00

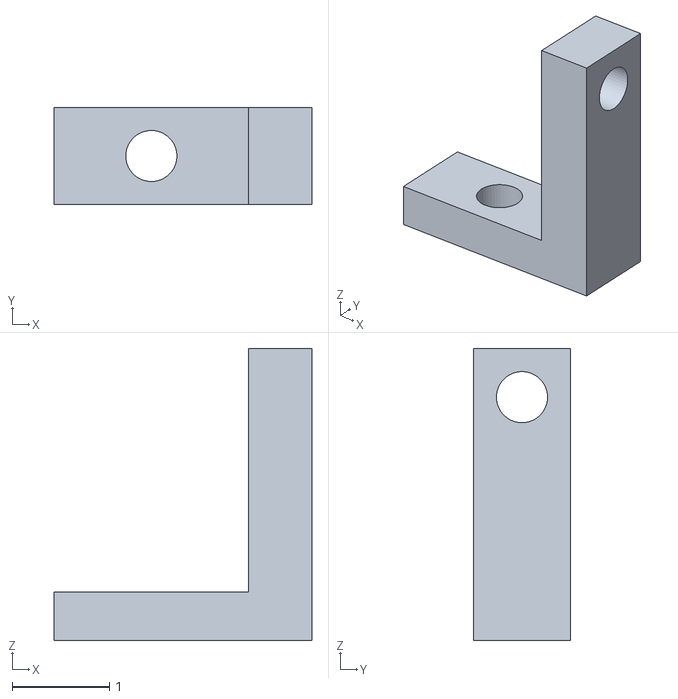
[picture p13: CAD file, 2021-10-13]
subsystems/housing/hardware/fabrication/growtray/growtray_nozzlemount_a.stl
2.65 x 1.00 x 3.00

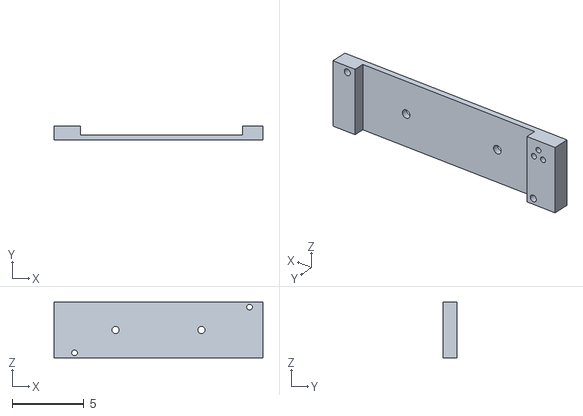
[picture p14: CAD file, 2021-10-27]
subsystems/housing/hardware/fabrication/lightingtray/lighting_driver_mount.stl
14.6 x 1 x 3.91

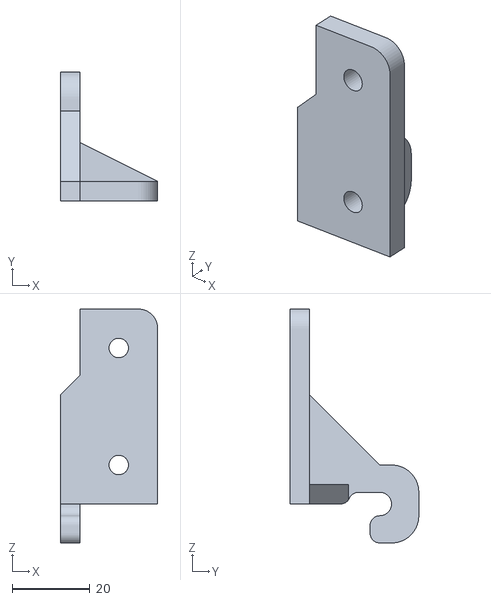
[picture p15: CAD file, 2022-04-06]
subsystems/housing/hardware/fabrication/trayhook_backleft.stl
25.0 x 33.0 x 60.0

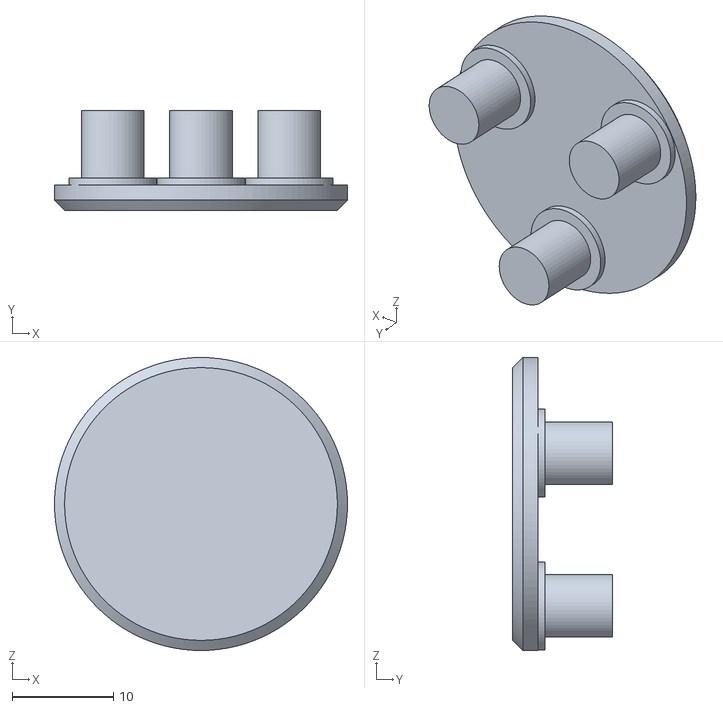
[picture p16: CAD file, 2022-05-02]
subsystems/aeroponics/hardware/dosagepump/fabrication/dosagepump_roller_lower.stl
29.0 x 9.85 x 29.0

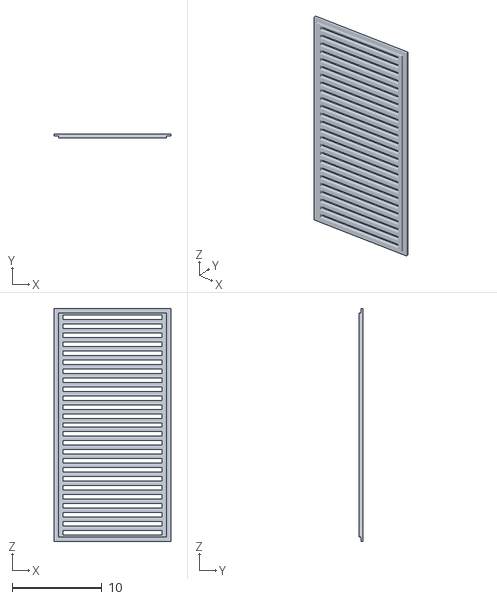
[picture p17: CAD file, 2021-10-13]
subsystems/dehumidification/hardware/fabrication/CartridgeLid.stl
13.0 x 0.5 x 26.0

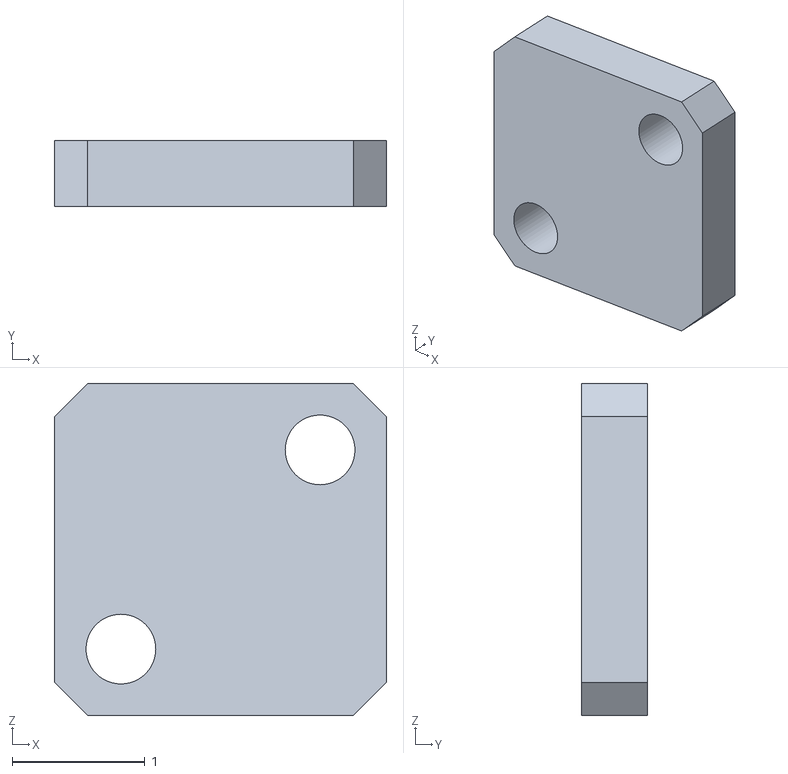
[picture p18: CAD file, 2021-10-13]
subsystems/housing/hardware/fabrication/brackets/bracket_diagonal.stl
2.50 x 0.5 x 2.50

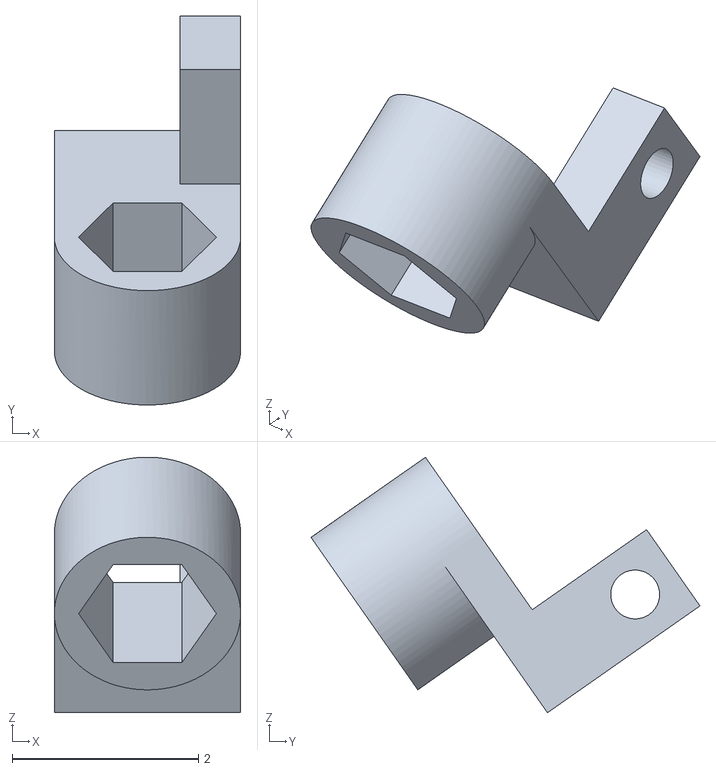
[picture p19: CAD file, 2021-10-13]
subsystems/housing/hardware/fabrication/growtray/growtray_nozzlemount_b.stl
2.00 x 4.18 x 2.74

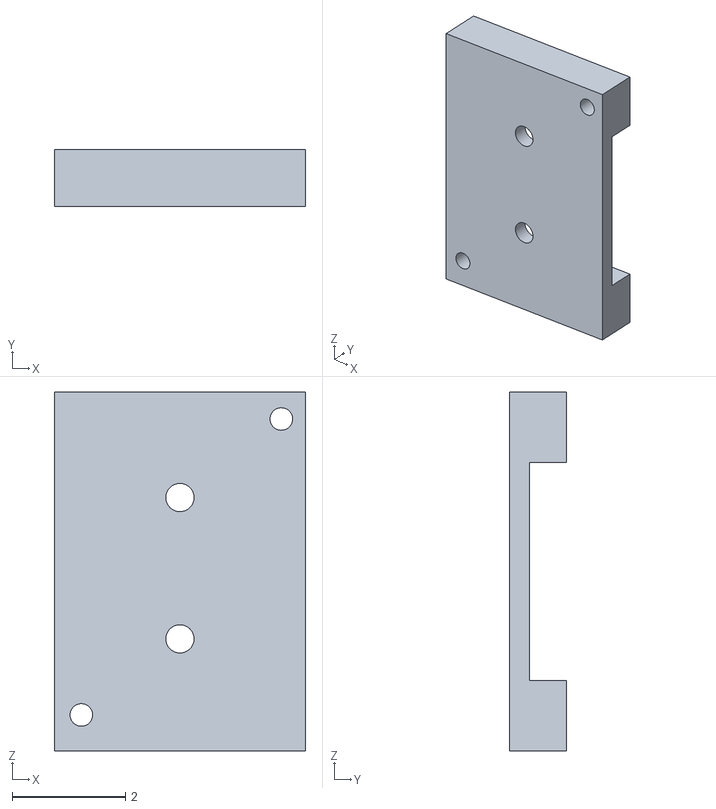
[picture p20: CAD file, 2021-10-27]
subsystems/housing/hardware/fabrication/lightingtray/lighting_led_mount.stl
4.44 x 1.00 x 6.35

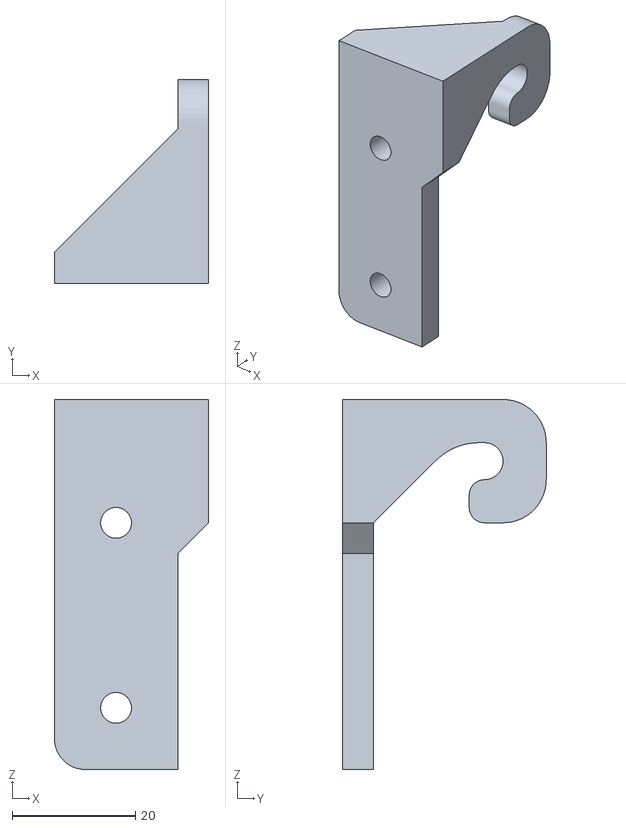
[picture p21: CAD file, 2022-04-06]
subsystems/housing/hardware/fabrication/trayhook_frontright.stl
25.0 x 33.0 x 60.0

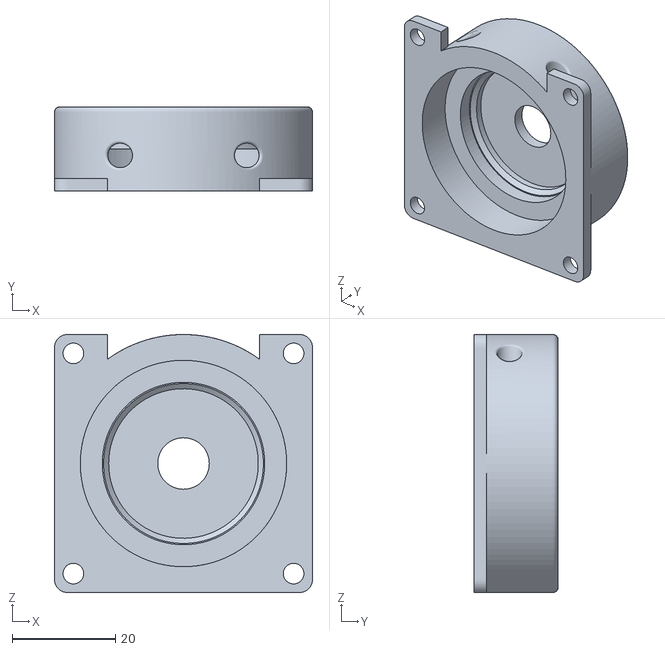
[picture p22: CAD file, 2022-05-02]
subsystems/aeroponics/hardware/dosagepump/fabrication/dosagepump_body_upper.stl
50.0 x 16.4 x 50.0

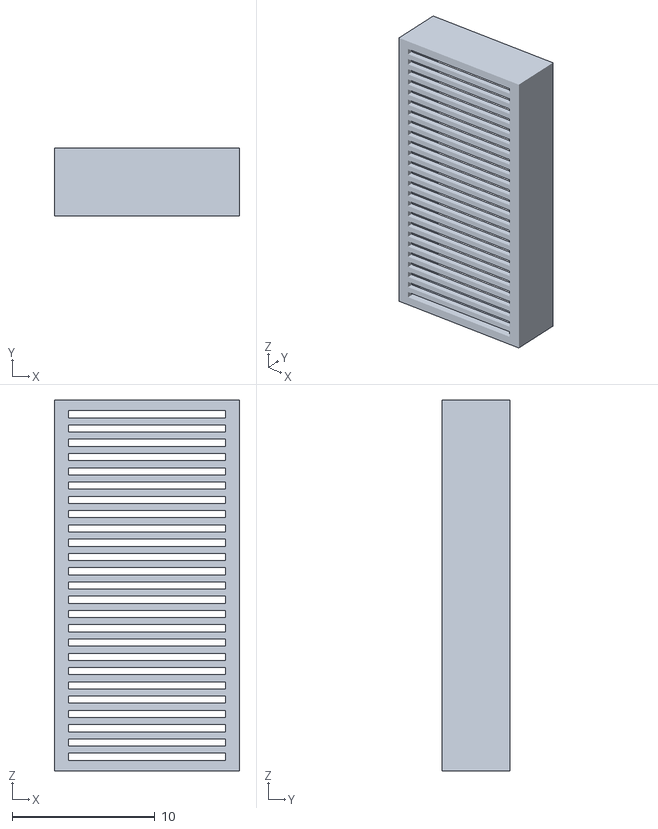
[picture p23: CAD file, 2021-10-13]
subsystems/dehumidification/hardware/fabrication/Cartridge.stl
13.0 x 4.75 x 26.0

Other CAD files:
subsystems/housing/hardware/fabrication/brackets/bracket_t.stl
subsystems/housing/hardware/fabrication/trayhook_frontleft.stl
subsystems/aeroponics/hardware/dosagepump/fabrication/dosagepump_roller_upper.stl
subsystems/housing/hardware/fabrication/brackets/bracket_l.stl
subsystems/housing/hardware/fabrication/feet.stl
subsystems/housing/hardware/fabrication/growtray/growtray_plate_quarter.stl
subsystems/housing/hardware/fabrication/growtray/growtray_plate_washer.stl
subsystems/housing/hardware/fabrication/trayhook_backright.stl

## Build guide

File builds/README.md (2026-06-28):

# PeaPod Builds

All builds, each representing an implementation-specific formulation of the PeaPod framework, per-unit.

## Folder Structure

All builds will follow the same folder structure:

- `assets/` - various graphical/etc. assets (diagrams, etc. excluding pictures of schematics/PCB layouts)
- `docs/` - build-specific documentation (user manuals, build guides, quick-start, product briefs, etc.)
- `hardware/` - compiled BoMs, including fabrication (3D printing, PCB w/ gerber, etc.) and purchase (DigiKey, McMaster-Carr, etc.)

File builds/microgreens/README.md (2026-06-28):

# PeaPod for Microgreens

PeaPod for Microgreens is an implementation-specific formulation of the PeaPod framework, designed to repeatably grow high-quality microgreens at minimal operating cost. This repository contains all the necessary information to build and operate the PeaPod for Microgreens.

# Cost Breakdown

> Production & Revenue Estimate (Per Unit, 3 Trays, 1 Week Cycle): 2 lbs. (>$40)

## Materials

> Aeroponic Supply System can provide water for up to 4 trays

  - Microgreen Tray: $400 ea.
  - Aeroponic Supply System: $400
  - Lighting System: $100 ea.
  - Power & Control: $100
  - Housing: $200

Total: $1200

Break-Even: 30 Weeks

## Labor

 - Design & Fabrication Fees
 - Manufacturing Labor
 - Assembly Labor
 - Delivery & Installation Labor
 - Setup & Training Fees

## Operating Costs

 - Electricity
 - Water
 - Fertilizer (optional)
 - Seeds
 - Operating Labor

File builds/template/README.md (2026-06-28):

# PeaPod for XYZ

PeaPod for XYZ is an implementation-specific formulation of the PeaPod framework, designed to lorem ipsum dolor sit amet, consectetur adipiscing elit. This repository contains all the necessary information to build and operate the PeaPod for XYZ.

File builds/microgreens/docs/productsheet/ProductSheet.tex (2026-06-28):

\documentclass{../../../docs/tex/report}
\usepackage{setspace} % Setting line spacing
\usepackage{ulem} % Underline
\usepackage{caption} % Captioning figures
\usepackage{subcaption} % Subfigures
\usepackage{geometry} % Page layout
\usepackage{multicol} % Columned pages
\usepackage{array,etoolbox}
\usepackage{fancyhdr}
\usepackage{enumitem}
\usepackage[toc,page]{appendix}
\setlist{noitemsep}

% Page layout (margins, size, line spacing)
\geometry{letterpaper, left=1in, right=1in, bottom=1in, top=1in}
\setstretch{1}

% Headers
\pagestyle{fancy}
\lhead{PeaPod for Microgreens}
\rhead{PeaPod Technologies Inc.}

\begin{document}

\begin{titlepage}
    \begin{center}
        \vspace*{1.2cm}

        \textbf{\large{PeaPod for Microgreens - Product Sheet}}

        \vspace{0.5cm}

        Low-Cost Modular High-Quality Microgreens Production System

        \vfill
        \input{../../../docs/tex/documentation/Namecard.tex}
        \vspace{1.25cm}

        Revision 0.1\\
        PeaPod Technologies Inc.\\
        March 31st, 2024

    \end{center}
\end{titlepage}

\thispagestyle{plain}

\tableofcontents
\clearpage

\section{Product Overview}

\subsection{Introduction}

PeaPod for Microgreens is a custom aeroponic plant growth unit optimized for growing high-quality microgreens at minimal operating cost. The system is designed to be turn-key and easy to use, from germination to harvest. Full-stack automation and control systems ensure repeatability and reliability, enabling business owners to make surefire return on investment, making this product ideal for in-house restaurant production and small-scale commercial growing.

\clearpage

% References
\bibliographystyle{IEEEtran}
\bibliography{references}
\end{document}

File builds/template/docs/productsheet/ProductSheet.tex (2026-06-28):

\documentclass{../../../../docs/tex/report}
\usepackage{setspace} % Setting line spacing
\usepackage{ulem} % Underline
\usepackage{caption} % Captioning figures
\usepackage{subcaption} % Subfigures
\usepackage{geometry} % Page layout
\usepackage{multicol} % Columned pages
\usepackage{array,etoolbox}
\usepackage{fancyhdr}
\usepackage{enumitem}
\usepackage[toc,page]{appendix}
\setlist{noitemsep}

% Page layout (margins, size, line spacing)
\geometry{letterpaper, left=1in, right=1in, bottom=1in, top=1in}
\setstretch{1}

% Headers
\pagestyle{fancy}
\lhead{PeaPod XYZ}
\rhead{PeaPod Technologies Inc.}

\begin{document}

\begin{titlepage}
    \begin{center}
        \vspace*{1.2cm}

        \textbf{\large{PeaPod XYZ - Product Sheet}}

        \vspace{0.5cm}

        Lorem ipsum dolor sit amet, consectetur adipiscing elit.

        \vfill
        \input{../../../docs/tex/documentation/Namecard.tex}
        \vspace{1.25cm}

        Revision 0.1\\
        PeaPod Technologies Inc.\\
        Month XX, 2024

    \end{center}
\end{titlepage}

\thispagestyle{plain}

\tableofcontents
\clearpage

\section{Product Overview}

\subsection{Introduction}

Lorem ipsum dolor sit amet, consectetur adipiscing elit. Sed auctor, nunc nec ultricies ultricies, nunc nunc ultricies nunc, nec ultricies nunc nunc nec. Sed auctor, nunc nec ultricies ultricies, nunc nunc ultricies nunc, nec ultricies nunc nunc nec. Sed auctor, nunc nec ultricies ultricies, nunc nunc ultricies nunc, nec ultricies nunc nunc nec. Sed auctor, nunc nec ultricies ultricies, nunc nunc ultricies nunc, nec ultricies nunc nunc nec.

\clearpage

% References
\bibliographystyle{IEEEtran}
\bibliography{references}
\end{document}

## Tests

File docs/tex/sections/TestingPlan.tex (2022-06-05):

\section{Testing Plan}
% Per-requirement testing plan
% Processes, measurements, experiments
% NOTE: Often, acceptable ranges in results depend on specifics of the technology

\subsection{Acceptability of Outputs}
% Are people willing to eat output? Incl. appearance, aroma, flavor, and texture
% Specific preparation and/or incorporation of output (formulation) for tasting

\subsubsection{Testing Procedure}
% How will this requirement be tested within the context of your specific technology?
% Suggestion: Double-blind volunteer study
Tested via blind studies where participants are divided into two groups and given either control outputs (i.e. established commercial product) or test outputs (i.e. produced by PeaPod). Participants will rate outputs on 4 criteria (appearance, aroma, flavour, and texture) on a 9-point scale.

To simulate acceptability over a long period of time, it will be important to study outputs with consideration for how the subjects will interact with them. This includes varying preparation methods (fresh, cooked, dehydrated, etc.) and preparing combinations of foods both purely with PeaPod outputs and with external foods that would be available in the field.

Blind studies are eminent in consumer testing as they allow researchers to get a completely unbiased dataset. Special care needs to be taken when presenting, preparing, and collecting samples for testing to ensure researchers do not influence results. Ideally, resources will permit a double-blind study where researchers hire an outside entity to conduct the test and return results with generic labels.

The 9-point scale originates from U.S. Army testing, where it was developed using language which has roughly equal psychological distances between points on the scale. While the use of 9 points is otherwise arbitrary, there exists a large history of research validating its analytical use in long-term food production \cite{hedonic}.

\textbf{1382 Characters} (Maximum 4000)

\subsubsection{Sample Collection Schedule}
% How many days/ cycles will the system be in operation before samples can be collected, to clearly assess the above criteria? Please provide a description of the process for sample collection (including size, timing and number of samples), packaging, and shipping.

%to address acceptability, will need a variety of things at a variety of qualities based on real distributions

To test acceptability of a long-term food solution, it is important to test the entire spectrum of output quality at a good-faith approximation of its distribution. This means instead of testing 'good' control outputs against 'good' PeaPod outputs, we will need to test batches of control outputs (at a naturally-arising quality distribution) vs. batches of PeaPod outputs (again, at a quality distribution). This allows for holistic comparison of the technology's performance as well as end user experience as opposed to specific comparison of individual items.

To employ statistical analysis, a sample size of at least $n=30$ will be collected for each crop, with the collection time dependent on the crop. For initial tests, crops will be collected at a developmental stage roughly equivalent to control crops purchased at a store. For further tests, the crops can be collected at the point PeaPod's analytical tools determine is optimal. Packaging and shipping will be done according to existing best practices, with care to package more than necessary as a factor of safety. 

\textbf{1079 Characters} (Maximum 4000)

\clearpage

\subsection{Safety of Process and Outputs}
% SPECIFICALLY food production area
% Chemical hazards - Toxins, heavy metals (As, Cd, Hg, Pb, etc.)
% Biohazards - total aerobic plate count, ATP testing of food contact surfaces
% TODO: What do those^ mean? How do we test them?

% NOT materials, NOT the system itself
% Cleaning, disinfection (chemical selection and frequency), harvesting/crew interaction procedures
% !! Mitigation of threats both pre-flight (sterilization and packaging) and in the field (minimal testing, minimal crew interaction)

\subsubsection{Testing Procedure}
% How will this requirement be tested within the context of your specific technology?

Given the environment in which PeaPod will operate, process safety will be developed on the foundation of prevention. This is because crisis response and containment is severely limited in the confines of space: identification often requires propagation of the threat (i.e. incubation of potential pathogens for colony count), and quarantine is more difficult and loses a larger proportion of food than it does on Earth.

This begins pre-flight, as all materials - especially biological - are sanitized, tested, and packaged in isolation so a breach contaminates as little product as possible. Once everything is installed in the field, the design principles of the entire system take over as methods of prevention. By employing key design principles such as minimal interaction, PeaPod mitigates the introduction of foreign substances and, in turn, the ingress of potential threats. Interaction will only occur at times of harvest and planting, which double as times of cleaning and sanitation. 

For testing the UX of the processes, using established space station procedures, subjects will harvest and clean product, clean all surfaces, sanitize all surfaces, and plant surface-sterilized seeds.

As for non-biological threats such as heavy metals or other toxins, careful selection and sourcing of construction materials will eliminate most threats to the system. As a regular maintenance measure, flushing of the water and air supplies through the space station's recycling system will prevent buildup by keeping them up to external standards.

\textbf{Chemical Hazards}\\
As part of PeaPod's design principle regarding prevention, all sourcing of parts and resources has been done with inherent, chemical threats in mind (lead-free solder and electronic components, food-safe fittings and parts for aeroponics, etc.). As a result, the default construction of the unit poses no threat for chemicals or other toxins to enter the biological system or its surroundings.

The other source of potential threats is during crew interaction steps when they harvest, clean, sanitize, and plant. To protect against hazards, PeaPod's maintenance steps follow carefully designed HACCP protocols and use food-safe cleansers and sanitizers.

% All static materials, inputs (nutrients, pH)

\textbf{Biological Hazards}\\
There are no biological hazards inherent to the PeaPod system. Plant species selection should be performed carefully to ensure safety according to mission requirements.

Aerobic Plate Count (APC) testing to be done with the Conventional Plate Count Method outlined by the FDA \cite{platecount}. This is selected over the Spiral Plate Method as it is inexpensive and uses many household materials. The goal of APC testing is to indicate the bacterial population in food-adjacent sections of the design. Results to be compared against STD-3001 to ensure a maximum of 3000 colony forming units/square ft. Colony forming units appear as distinct ``blobs'' of bacteria on a growth material, indicating the relative abundance of viable bacteria on a given surface.

\textbf{Food Outputs}
% Biohazards - total aerobic count, specific pathogens (enterobacteriaceae, salmonella, yeasts, molds, E. coli, Listeria, etc.)

% So long as all threats are mitigated for both process and materials/inputs, food outputs should be safe
APC testing conducted on samples as outlined for biological hazards to ensure bacterial population below 20 000 CFU/g per STD-3001. \textit{Enterobacteriaceae} have a population limit of 100 CFU/g per STD-3001, and can be tested via a rapid test such as the MicroSnap EB. Similarly, testing for salmonella will be performed using a rapid detection kit to ensure a population of 0 CFU/g. Finally, testing for yeasts and molds will be performed with a testing kit to to ensure a population count below 1000 CFU/g.

Given the wide use cases for crops (raw/dried, cut/whole, fresh/preserved) it will be important to conduct tests on each use case to see if results remain acceptable. For example, higher surface area crops are intrinsically more susceptible to bacterial growth per gram. So, crops prior to testing will be processed in the same way they would be before consumption in order to validate realistic operating conditions.
%microsnap source: https://www.hygiena.com/food-safety-solutions/indicator-organisms/microsnap-enterobacteriaceae/

% Seeds (seed cleaning and disinfection, packaging)

\textbf{By-Product Outputs}
By-product outputs fall into two cateogries, air exhaust and inedible matter. Air will be filtered and dehumidified to ambient levels by the gas exchange system, ensuring it is safe for the local environment. Inedible matter will be tested in the same way as food outputs to ensure threats are not present in the system at all. Further threats would arise in the processing of by-products should they be used as a nutrient source in successive cycles. If this process is implemented, new testing procedures will be developed for it. Otherwise, threats are mitigated by disposal in the same manner as other biological substances such as human waste.

% maximum 4000 characters

\textbf{4036 Characters} (Maximum 4000)

\subsubsection{Sample Collection Schedule}
% How many days/ cycles will the system be in operation before samples can be collected, to clearly assess the above criteria? Please provide a description of the process for sample collection (including size, timing and number of samples), packaging, and shipping.
Safety testing will be conducted in tandem with collection of samples for acceptability, with key metrics being measured as successive rounds of crops are collected. Beyond number and size of samples, it will be critical to follow operating procedures as closely as possible. This is because of its two-fold interaction with crop quality and safety. The only deviation will be the measuring of metrics such as CFU count, as this is safe to do on Earth conditions.

Regardless of test results, crop collection will continue to see if the design's mitigation strategies are effective. For example, if Harvest 2 has allowable but present levels of \textit{Enterobacteriaceae}, it is important to see if it persists to Harvests 3 and 4 or if standard cleaning procedures manage to eliminate it.

Then, over the course of 30 or so harvests, the presence of hazards can be charted as a function of harvest number and cleaning cycles, allowing patterns to emerge and weaknesses to be found for long-duration missions. Testing for these hazards will be in line with the list above: bacteria via APC, organic residue via ATP testing, and chemical hazards via water supply analysis. Water supply testing is straightforward, with an abundance of commercial test strips available to identify any given substance.

\textbf{1172 Characters} (Maximum 4000)

\clearpage

\subsection{Resource Outputs}
% Nutritional analysis - macro- and micro-nutrients
% TODO: How to perform nutritional analysis?
% Really depends on plant selection. How do we know what the nutritional makeup of a given food product is at the time of harvest?

\subsubsection{Testing Procedure}
% How will this requirement be tested within the context of your specific technology?

Personally testing nutritional makeup of outputs is far beyond the resources and scope of this project. Instead, a variety of outputs will be produced and shipped to an external, ISO-17025 certified lab such as SGS Canada for testing.

While this is useful for validation on Earth, it fails to address the issue of analysis at time of harvest. To tackle this, PeaPod will use data collected on Earth-bound trials in combination with lab analysis and existing datasets to develop a way of predicting crop quality during the growing process. By applying algorthmic prediction, we can optimize resource output efficiency by, for example, marking crops that show early signs of failure for replacement. This helps maximize the output to input ratio by cutting losses earlier and with less labour cost than people would be able to.

% There are no inherent micro- or macro-nutritional limitations imposed by the system and its food outputs.

\textbf{826 Characters} (Maximum 4000)

\subsubsection{Sample Collection Schedule}
% How many days/ cycles will the system be in operation before samples can be collected, to clearly assess the above criteria? Please provide a description of the process for sample collection (including size, timing and number of samples), packaging, and shipping.

The number of days required for sample collection is entirely dependent on what sample is being produced. For one-time growth products, such as carrots or lettuce, the days required is exactly the time to harvest of the plant. Size of collection is dependent on how many units are run at the same time. For plants that produce products multiple times, such as beans or tomatoes, samples should be collected after each production cycle. This means the time required to collect n samples is C + n*X, where C is the initial growth period of the plant and X the time between harvests. It is important to collect multiple subsequent harvests in order to see the relationship between this and produce quality.

Packaging and shipping will be done according to freight standards of the carrier being used, such as \cite{shipping}. 

% Sample collection procedure?
% Collect non-edible plant matter (roots, stems, leaves, flowers, etc.) for safety testing

\textbf{824 Characters} (Maximum 4000)

\clearpage

\subsection{Reliability and Stability of Outputs}
% Biohazards - total aerobic plate count, enterobacteriaceae, yeasts, molds
%is this not the same as safety of outputs?

% Fresh produce is inherently non-shelf-stable
% What preservation methods are available to us (refrigeration?)
% Staggering planting times so that harvests happen at regular intervals

\subsubsection{Testing Procedure}
% How will this requirement be tested within the context of your specific technology?

PeaPod's outputs are fresh produce, and as such are intended for consumption as soon as possible after harvest and preparation. Any product not immediately consumed post preparation should be stored in an airtight package and kept below 12.5°C to prolong shelf life and maintain acceptability. Certain products of PeaPod have the possibility of being dehydrated to further increase their shelf life.

To mitigate the need for long duration food storage, growth cycles should be staggered to periodically supply fresh produce when astronauts are ready to eat.

\textbf{558 Characters} (Maximum 4000)

\subsubsection{Sample Collection Schedule}
% How many days/ cycles will the system be in operation before samples can be collected, to clearly assess the above criteria? Please provide a description of the process for sample collection (including size, timing and number of samples), packaging, and shipping.

Collection time is not a critical variable for this test, however safe storage time is. To quantify it, a variety of outputs can be compared to their control equivalents to identify any disparities in shelf life---be it raw, dehydrated and cooled, or airtight and cooled.

The number of cycles necessary to complete testing will be equivalent to the number of items tested. Each of these three storage methods should be tested for a variety of plant species and yield types over a number of trials to minimize randomness.

Criteria for shelf life will include acceptability as a function of time, quantity/existence of bacteria, and the relationship between crew time and quality of output.

\textbf{690 Characters} (Maximum 4000)

\clearpage

\subsection{Additional Comments}
% Days/cycles of operation before sample collection?
% Incl. sample collection (size, timing, quantity), packaging, shipping

% Maximum 4000 characters

\clearpage

\input{../tex/Materials.tex}

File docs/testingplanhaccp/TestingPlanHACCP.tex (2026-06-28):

\documentclass{../tex/report}
\usepackage{setspace} % Setting line spacing
\usepackage{ulem} % Underline
\usepackage{caption} % Captioning figures
\usepackage{subcaption} % Subfigures
\usepackage{geometry} % Page layout
\usepackage{multicol} % Columned pages
\usepackage{multirow}
\usepackage{array,etoolbox}
\usepackage{fancyhdr}
\usepackage{enumitem}
\usepackage{tabularx}
\usepackage[toc,page]{appendix}
\setlist{noitemsep}

% Page layout (margins, size, line spacing)
\geometry{letterpaper, left=1in, right=1in, bottom=1in, top=1in}
\setstretch{1}

% Headers
\pagestyle{fancy}
\lhead{PeaPod - Testing Plan \& HACCP Plan}
\rhead{PeaPod Technologies Inc.}

\begin{document}

\begin{titlepage}
    \begin{center}
        \vspace*{1.2cm}

        \textbf{\large{PeaPod - Testing Plan and\\Hazard Analysis and Critical Control Points (HACCP) Plan}}

        \vspace{0.5cm}

        NASA/CSA Deep Space Food Challenge Phase 2

        \vfill
        \input{../tex/documentation/Namecard.tex}
        \vspace{1.25cm}

        Revision 1.0\\
        PeaPod Technologies Inc.\\
        May 31st, 2022

    \end{center}
\end{titlepage}

\thispagestyle{plain}

\tableofcontents
\clearpage

\input{../tex/TestingPlan.tex}

\clearpage

\input{../tex/HACCP.tex}

\clearpage

\section{Feedback}
% Is there any feedback you would like to share with the Challenge Team? Do you have specific requests for topics, experts or information you would like to see discussed in the Phase 2 workshops?

No feedback is provided.

% Maximum 5000 characters

\clearpage

% References
\bibliographystyle{IEEEtran}
\bibliography{references}
\end{document}

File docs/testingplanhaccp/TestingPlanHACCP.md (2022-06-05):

# Testing Plan

## Acceptability of Outputs

### Testing Procedure

Tested via blind studies where participants are divided into two groups and given either control outputs (i.e. established commercial product) or test outputs (i.e. produced by PeaPod). Participants will rate outputs on 4 criteria (appearance, aroma, flavour, and texture) on a 9-point scale.

To simulate acceptability over a long period of time, it will be important to study outputs with consideration for how the subjects will interact with them. This includes varying preparation methods (fresh, cooked, dehydrated, etc.) and preparing combinations of foods both purely with PeaPod outputs and with external foods that would be available in the field.

Blind studies are eminent in consumer testing as they allow researchers to get a completely unbiased dataset. Special care needs to be taken when presenting, preparing, and collecting samples for testing to ensure researchers do not influence results. Ideally, resources will permit a double-blind study where researchers hire an outside entity to conduct the test and return results with generic labels.

The 9-point scale originates from U.S. Army testing, where it was developed using language which has roughly equal psychological distances between points on the scale. While the use of 9 points is otherwise arbitrary, there exists a large history of research validating its analytical use in long-term food production.

### Sample Collection Schedule

To test acceptability of a long-term food solution, it is important to test the entire spectrum of output quality at a good-faith approximation of its distribution. This means instead of testing 'good' control outputs against 'good' PeaPod outputs, we will need to test batches of control outputs (at a naturally-arising quality distribution) vs. batches of PeaPod outputs (again, at a quality distribution). This allows for holistic comparison of the technology's performance as well as end user experience as opposed to specific comparison of individual items.

To employ statistical analysis, a sample size of at least n=30 will be collected for each crop, with the collection time dependent on the crop. For initial tests, crops will be collected at a developmental stage roughly equivalent to control crops purchased at a store. For further tests, the crops can be collected at the point PeaPod's analytical tools determine is optimal. Packaging and shipping will be done according to existing best practices, with care to package more than necessary as a factor of safety.

## Safety of Process and Outputs

### Testing Procedure

Given the environment in which PeaPod will operate, process safety will be developed on the foundation of prevention. This is because crisis response and containment is severely limited in the confines of space: identification often requires propagation of the threat (i.e. incubation of potential pathogens for colony count), and quarantine is more difficult and loses a larger proportion of food than it does on Earth.

This begins pre-flight, as all materials---especially biological---are sanitized, tested, and packaged in isolation so a breach contaminates as little product as possible. Once everything is installed in the field, the design principles of the entire system take over as methods of prevention. By employing key design principles such as minimal interaction, PeaPod mitigates the introduction of foreign substances and, in turn, the ingress of potential threats. Interaction will only occur at times of harvest and planting, which double as times of cleaning and sanitation.

For testing the UX of the processes, using established space station procedures, subjects will harvest and clean product, clean all surfaces, sanitize all surfaces, and plant surface-sterilized seeds.

As for non-biological threats such as heavy metals or other toxins, careful selection and sourcing of construction materials will eliminate most threats to the system. As a regular maintenance measure, flushing of the water and air supplies through the space station's recycling system will prevent buildup by keeping them up to external standards.

**Chemical Hazards**
As part of PeaPod's design principle regarding prevention, all sourcing of parts and resources has been done with inherent, chemical threats in mind (lead-free solder and electronic components, food-safe fittings and parts for aeroponics, etc.). As a result, the default construction of the unit poses no threat for chemicals or other toxins to enter the biological system or its surroundings.

The other source of potential threats is during crew interaction steps when they harvest, clean, sanitize, and plant. To protect against hazards, PeaPod's maintenance steps follow carefully designed HACCP protocols and use food-safe cleansers and sanitizers.

**Biological Hazards**
There are no biological hazards inherent to the PeaPod system. Plant species selection should be performed carefully to ensure safety according to mission requirements.

Aerobic Plate Count (APC) testing to be done with the Conventional Plate Count Method outlined by the FDA. This is selected over the Spiral Plate Method as it is inexpensive and uses many household materials. The goal of APC testing is to indicate the bacterial population in food-adjacent sections of the design. Results to be compared against STD-3001 to ensure a maximum of 3000 colony forming units/square ft. Colony forming units appear as distinct "blobs" of bacteria on a growth material, indicating the relative abundance of viable bacteria on a given surface.

**Food Outputs**
APC testing conducted on samples as outlined for biological hazards to ensure bacterial population below 20 000 CFU/g per STD-3001. *Enterobacteriaceae* have a population limit of 100 CFU/g per STD-3001, and can be tested via a rapid test such as the MicroSnap EB. Similarly, testing for salmonella will be performed using a rapid detection kit to ensure a population of 0 CFU/g. Finally, testing for yeasts and molds will be performed with a testing kit to to ensure a population count below 1000 CFU/g.

Given the wide use cases for crops (raw/dried, cut/whole, fresh/preserved) it will be important to conduct tests on each use case to see if results remain acceptable. For example, higher surface area crops are intrinsically more susceptible to bacterial growth per gram. So, crops prior to testing will be processed in the same way they would be before consumption in order to validate realistic operating conditions.

**By-Product Outputs** 
By-product outputs fall into two cateogries, air exhaust and inedible matter. Air will be filtered and dehumidified to ambient levels by the gas exchange system, ensuring it is safe for the local environment. Inedible matter will be tested in the same way as food outputs to ensure threats are not present in the system at all. Further threats would arise in the processing of by-products should they be used as a nutrient source in successive cycles. If this process is implemented, new testing procedures will be developed for it. Otherwise, threats are mitigated by disposal in the same manner as other biological substances such as human waste.

### Sample Collection Schedule

Safety testing will be conducted in tandem with collection of samples for acceptability, with key metrics being measured as successive rounds of crops are collected. Beyond number and size of samples, it will be critical to follow operating procedures as closely as possible. This is because of its two-fold interaction with crop quality and safety. The only deviation will be the measuring of metrics such as CFU count, as this is safe to do on Earth conditions.

Regardless of test results, crop collection will continue to see if the design's mitigation strategies are effective. For example, if Harvest 2 has allowable but present levels of *Enterobacteriaceae*, it is important to see if it persists to Harvests 3 and 4 or if standard cleaning procedures manage to eliminate it.

Then, over the course of 30 or so harvests, the presence of hazards can be charted as a function of harvest number and cleaning cycles, allowing patterns to emerge and weaknesses to be found for long-duration missions. Testing for these hazards will be in line with the list above: bacteria via APC, organic residue via ATP testing, and chemical hazards via water supply analysis. Water supply testing is straightforward, with an abundance of commercial test strips available to identify any given substance.

## Resource Outputs

### Testing Procedure

Personally testing nutritional makeup of outputs is far beyond the resources and scope of this project. Instead, a variety of outputs will be produced and shipped to an external, ISO-17025 certified lab such as SGS Canada for testing.

While this is useful for validation on Earth, it fails to address the issue of analysis at time of harvest. To tackle this, PeaPod will use data collected on Earth-bound trials in combination with lab analysis and existing datasets to develop a way of predicting crop quality during the growing process. By applying algorthmic prediction, we can optimize resource output efficiency by, for example, marking crops that show early signs of failure for replacement. This helps maximize the output to input ratio by cutting losses earlier and with less labour cost than people would be able to.

### Sample Collection Schedule

The number of days required for sample collection is entirely dependent on what sample is being produced. For one-time growth products, such as carrots or lettuce, the days required is exactly the time to harvest of the plant. Size of collection is dependent on how many units are run at the same time. For plants that produce products multiple times, such as beans or tomatoes, samples should be collected after each production cycle. This means the time required to collect n samples is C + n\*X, where C is the initial growth period of the plant and X the time between harvests. It is important to collect multiple subsequent harvests in order to see the relationship between this and produce quality.

Packaging and shipping will be done according to freight standards for perishables of the carrier being used, such as those outlined by FedEx.

## Reliability and Stability of Outputs

### Testing Procedure

PeaPod's outputs are fresh produce, and as such are intended for consumption as soon as possible after harvest and preparation. Any product not immediately consumed post preparation should be stored in an airtight package and kept below 12.5°C to prolong shelf life and maintain acceptability. Certain products of PeaPod have the possibility of being dehydrated to further increase their shelf life.

To mitigate the need for long duration food storage, growth cycles should be staggered to periodically supply fresh produce when astronauts are ready to eat.

### Sample Collection Schedule

Collection time is not a critical variable for this test, however safe storage time is. To quantify it, a variety of outputs can be compared to their control equivalents to identify any disparities in shelf life---be it raw, dehydrated and cooled, or airtight and cooled.

The number of cycles necessary to complete testing will be equivalent to the number of items tested. Each of these three storage methods should be tested for a variety of plant species and yield types over a number of trials to minimize randomness.

Criteria for shelf life will include acceptability as a function of time, quantity/existence of bacteria, and the relationship between crew time and quality of output.

# Feedback

No feedback is provided.

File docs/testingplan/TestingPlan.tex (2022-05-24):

\documentclass{../tex/report}
\usepackage{setspace} % Setting line spacing
\usepackage{ulem} % Underline
\usepackage{caption} % Captioning figures
\usepackage{subcaption} % Subfigures
\usepackage{geometry} % Page layout
\usepackage{multicol} % Columned pages
\usepackage{array,etoolbox}
\usepackage{fancyhdr}
\usepackage{enumitem}
\usepackage[toc,page]{appendix}
\setlist{noitemsep}

% Page layout (margins, size, line spacing)
\geometry{letterpaper, left=1in, right=1in, bottom=1in, top=1in}
\setstretch{1}

% Headers
\pagestyle{fancy}
\lhead{PeaPod - Testing Plan}
\rhead{PeaPod Technologies Inc.}

\begin{document}

\begin{titlepage}
    \begin{center}
        \vspace*{1.2cm}

        \textbf{\large{PeaPod - Testing Plan}}

        \vspace{0.5cm}

        NASA/CSA Deep Space Food Challenge Phase 2

        \vfill
        \input{../tex/Namecard.tex}
        \vspace{.75cm}

        Revision 0.1\\
        PeaPod Technologies Inc.\\
        January 9th, 2022

    \end{center}
\end{titlepage}

\thispagestyle{plain}

\tableofcontents
\newpage

\input{../tex/TestingProcedure.tex}

\input{../tex/HACCP.tex}

\newpage

% References
\bibliographystyle{IEEEtran}
\bibliography{references}
\end{document}

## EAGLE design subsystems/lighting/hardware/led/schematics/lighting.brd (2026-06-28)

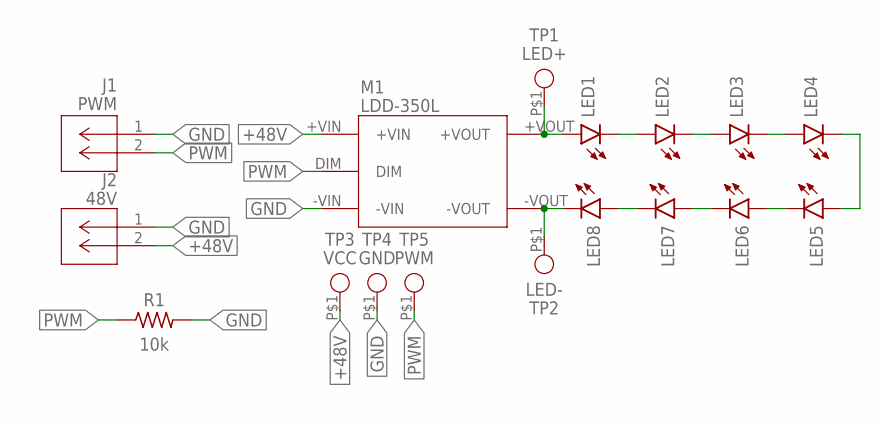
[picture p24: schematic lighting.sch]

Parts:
J1: PWM; 2PIN
J2: 48V; 2PIN
LED1, LED2, LED3, LED4, LED5, LED6, LED7, LED8: XLAMP_XP-G3_ROYAL; XLAMP_XP-G3
M1: LDD-350L; LDD-L
R1: 10k; RESC1608X60
TP1: LED+; TP_CIRCLE_2.5MM
TP2: LED-; TP_CIRCLE_2.5MM
TP3: VCC; TP_CIRCLE_2.5MM
TP4: GND; TP_CIRCLE_2.5MM
TP5: PWM; TP_CIRCLE_2.5MM

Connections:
+48V: J2.2, M1.+VIN, TP3.P$1
GND: J1.1 (2), J2.1, M1.-VIN, R1.2, TP4.P$1
unnamed: LED1.P$1 (A), M1.+VOUT, TP1.P$1
unnamed: LED1.P$2 (C), LED2.P$1 (A)
unnamed: LED2.P$2 (C), LED3.P$1 (A)
unnamed: LED3.P$2 (C), LED4.P$1 (A)
unnamed: LED4.P$2 (C), LED5.P$1 (A)
unnamed: LED5.P$2 (C), LED6.P$1 (A)
unnamed: LED6.P$2 (C), LED7.P$1 (A)
unnamed: LED7.P$2 (C), LED8.P$1 (A)
unnamed: LED8.P$2 (C), M1.-VOUT, TP2.P$1
PWM: J1.2 (3), M1.DIM, R1.1, TP5.P$1

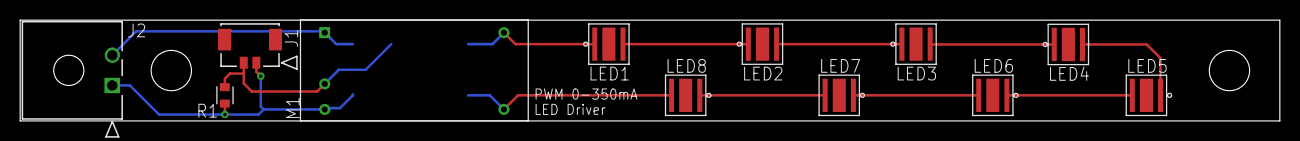
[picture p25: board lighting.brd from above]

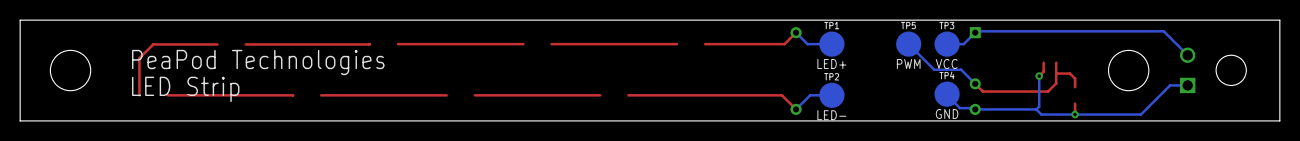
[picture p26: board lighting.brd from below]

Board: 2 copper layers, 125.0 x 10.0 mm, 17 parts (5 on the bottom side), 12 nets.

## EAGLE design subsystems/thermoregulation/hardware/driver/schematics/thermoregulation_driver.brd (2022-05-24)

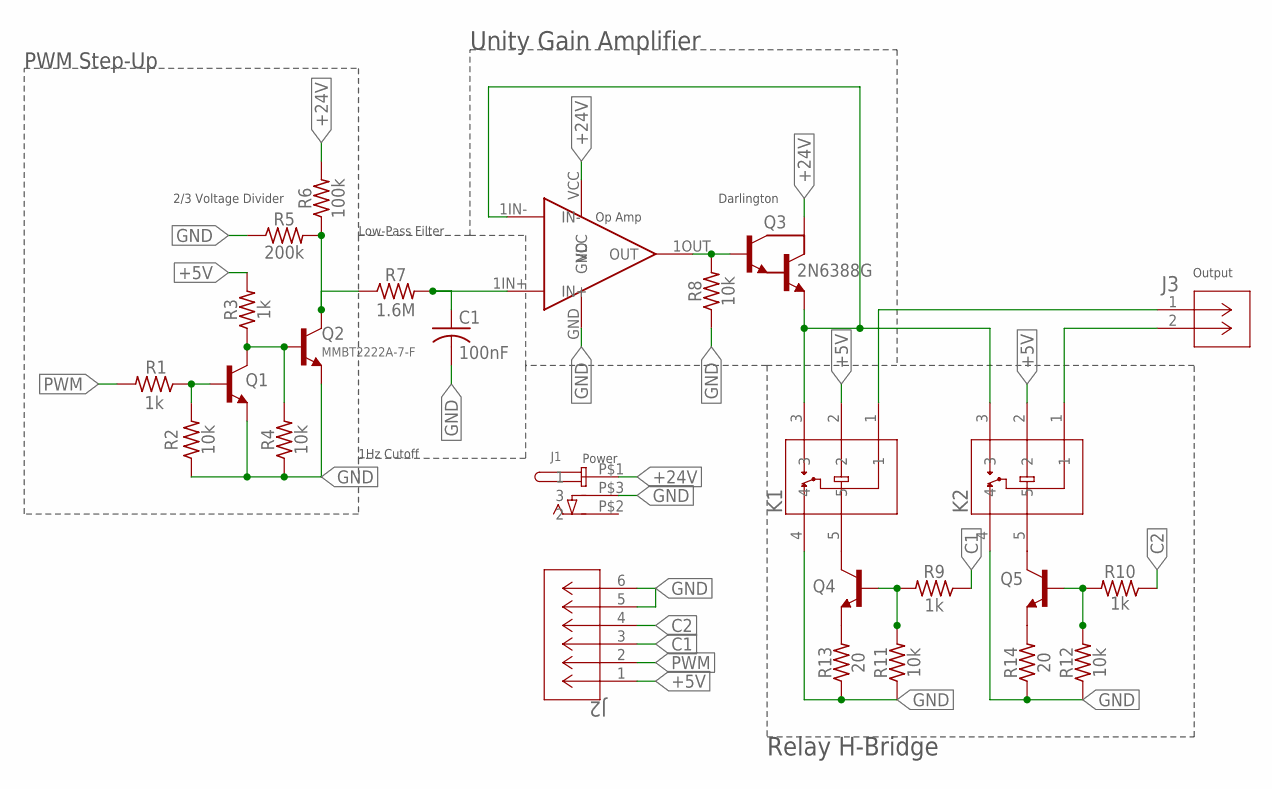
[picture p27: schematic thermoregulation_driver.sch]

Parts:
C1: 100nF; CAPC1005X60
J1: DCBARRELJACK
J2: MOLEX-MICROLOCK-6PIN; CON_5055670671
J3: 436500201CON_436500201_MOL; CON_436500201_MOL
K1, K2: G5LE-14_DC12RELAY_G5LE-1_DC5_OMR; RELAY_G5LE-1_DC5_OMR
OPAMP1: LM324N
Q1, Q4, Q5: NPN; SOT95P237X112-3N
Q2: MMBT2222A-7-F; SOT95P237X112-3N
Q3: 2N6388G; TO220
R1, R3, R9, R10: 1k; RESC1005X40
R2, R4, R8, R11, R12: 10k; RESC1005X40
R5: 200k; RESC1005X40
R6: 100k; RESC1005X40
R7: 1.6M; RESC1005X40
R13, R14: 20; RESC2012X65

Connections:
+5V: J2.1, K1.2, K2.2, R3.2
+24V: J1.P$1 (1), OPAMP1.VCC, Q3.C, R6.2
C1: J2.3, R9.1
C2: J2.4, R10.1
GND: C1.2, J1.P$3 (3), J2.5, J2.6, K1.4, K2.4, OPAMP1.GND, Q1.2 (E), Q2.2 (E), R2.1, R4.1, R5.1, R8.1, R11.1, R12.1, R13.1, R14.1
unnamed: Q2.3 (C), R5.2, R6.1, R7.1
unnamed: Q1.3 (C), Q2.1 (B), R3.1, R4.2
unnamed: C1.1, OPAMP1.1IN+ (IN+), R7.2
unnamed: OPAMP1.1OUT (OUT), Q3.B, R8.2
unnamed: Q1.1 (B), R1.1, R2.2
unnamed: K1.3, K2.3, OPAMP1.1IN- (IN-), Q3.E
unnamed: J3.1, K1.1
unnamed: J3.2, K2.1
unnamed: K1.5, Q4.3 (C)
unnamed: K2.5, Q5.3 (C)
unnamed: Q4.1 (B), R9.2, R11.2
unnamed: Q5.1 (B), R10.2, R12.2
unnamed: Q4.2 (E), R13.2
unnamed: Q5.2 (E), R14.2
PWM: J2.2, R1.2

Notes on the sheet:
PWM Step-Up
Low-Pass Filter
1Hz Cutoff
2/3 Voltage Divider
Unity Gain Amplifier
Darlington
Op Amp
Relay H-Bridge
Output
Power

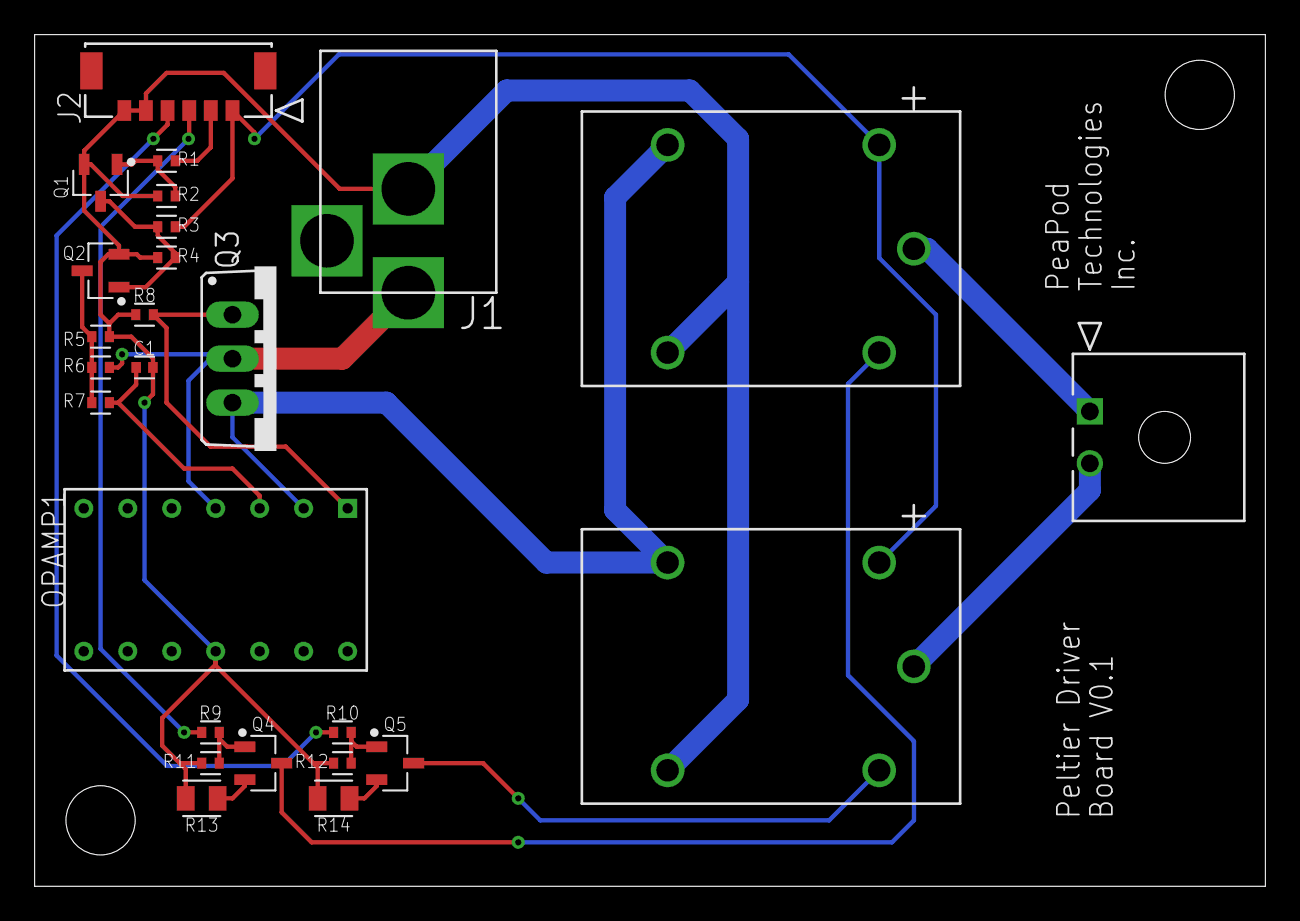
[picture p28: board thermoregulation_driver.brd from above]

Board: 2 copper layers, 71.1 x 49.2 mm, 26 parts (0 on the bottom side), 20 nets.

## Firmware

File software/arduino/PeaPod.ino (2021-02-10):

#include "SHT31.h"
#include "Sensor.h"
#include "Wire.h"
#include "K30.h"
#include "FloatSensor.h"
#include "Scale.h"

//MACRO DEFINITIONS
#define NUM_SENSORS 5
#define FLOATSENSOR_PIN 5
#define REVISION 0

//Setup
SHT31 sht31;
SHT31_temp temp = SHT31_temp(&sht31);
SHT31_hum hum = SHT31_hum(&sht31);
K30 k30;
Scale scale;
FloatSensor fs = FloatSensor(FLOATSENSOR_PIN);

unsigned int sensor = 0;

Sensor *sensors [NUM_SENSORS] = {
    &temp,
    &hum,
    &k30,
    &fs,
    &scale
};

void setup()
{
    digitalWrite(13, LOW);
    if(!post()){
        // Failed POST
        while(true){
            delay(250);
            digitalWrite(13, HIGH);
            delay(250);
            digitalWrite(13, LOW);
        }
    }

    // Tell computer 'ready', wait to receive valid program.
    Serial.println(0);

    String ins;
    do{
        while(!Serial.available());
        ins = Serial.readString();
        ins.trim();
    }while(!handleInstructions(ins));
    digitalWrite(13, HIGH);
}

void loop()
{
    if(Serial.available()){
        String in = Serial.readString();
        in.trim(); //Whitespace or newlines
        handleInstructions(in);
    }

    float read = sensors[sensor]->getRead();
    if(!isnan(read)){
        Serial.print("{\"type\":\"data\",\"msg\":{\"label\":\"");
        Serial.print(sensors[sensor]->evname);
        Serial.print("\",\"value\":");
        Serial.print(read);
        Serial.println("}}");
    }
    sensor = (sensor+1)%NUM_SENSORS;
    delay(1);
}

/**
 * Handles incoming instruction "var":value string.
 * @param s - Instruction string
 * @return was the instruction handled in a valid way?
 **/
bool handleInstruction(String in){
    uint8_t split = in.indexOf(":");
    if(split!=-1 && in.charAt(0) == '"' && in.charAt(split-1) == '"'){
        String var = in.substring(1, split-1); //Assumes surrounding ""
        float value = in.substring(split+1).toFloat();

        //INSTRUCTION HANDLING IF BLOCKS - EACH RETURNS TRUE
        if(var.equals("scale")){
            scale.calibrate(value);
            return true;
        }
        Serial.print("{\"type\":\"error\",\"msg\":\"Unknown target '");
        Serial.print(var);
        Serial.println("'\"}");
        return false;
    }
    Serial.print("{\"type\":\"error\",\"msg\":\"Failed to handle instruction '");
    in.replace("\"", "\\\"");
    Serial.print(in);
    Serial.println("'\"}");
    return false;
}

/**
 * Handles incoming instruction dictionary {"var":val,...}
 * Continues regardless of failure of a single instruction, alerts only
 * @param s - Instructions dictionary string
 * @return were all instructions handled in a valid way?
 * */
bool handleInstructions(String ins){
    if(ins.equals("{}")){
        return true;  //Empty dictionary, by default handled
    }
    if(ins.charAt(0) != '{' || ins.charAt(ins.length()-1) != '}'){
        Serial.print("{\"type\":\"error\",\"msg\":\"Invalid instructions dictionary '");
        Serial.print(ins);
        Serial.println("'\"}");
        return false;
    }
    ins = ins.substring(1, ins.length()-1); //Strips surrounding {}

    //Handles each individual instruction

    bool result = true;
    //While there are multiple instructions
    while(ins.indexOf(',') != -1){
        //Did the leftmost one succeed?
        result &= handleInstruction(ins.substring(0, ins.indexOf(',')));
        //Truncate leftmost instruction
        ins = ins.substring(ins.indexOf(',')+1);
    }
    //Handle last/only instruction (there are no commas left)
    result &= handleInstruction(ins);
    return result;
}

bool post(){
    Serial.begin(9600);
    while(!Serial); //Waits until serial opens

    // Test Serial protocol: send software revision byte, recieve check (0) byte or stop (!0) byte
    Serial.println(REVISION);
    while(!Serial.available());
    if(Serial.parseInt() != 0){
        return false;
    }

    // Test sensor protocols - per-sensor tests
    bool success = true;
    for(int i = 0; i < NUM_SENSORS; i++){
        bool latest = sensors[i]->begin();
        success &= latest;
        if(!latest){
            Serial.print("{\"type\":\"error\",\"msg\":\"Failed to initialize sensor '");
            Serial.print(sensors[i]->name);
            Serial.println("'. Check wiring.\"}");
        } else {
            Serial.print("{\"type\":\"debug\",\"msg\":\"Sensor '");
            Serial.print(sensors[i]->name);
            Serial.println("' initialized successfully.\"}");
        }
    }
    return success;
}

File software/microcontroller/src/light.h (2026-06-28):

#ifndef PEAPOD_LIGHT_H_
#define PEAPOD_LIGHT_H_

#include <peapod.h>

#define PEAPOD_MODULE_LIGHTING_EEPROM_CONTENTS {"[{\"24LC32\":[80],\"PCA9685\":[" STR(I2CIP_PCA9685_ADDRESS) "],\"ADS1115\":[" STR(I2CIP_ADS1115_ADDRESS) "]}]"}

#define PEAPOD_MODULE_LIGHTING_PWM_CHANNEL_RED PCA9685_CH0
#define PEAPOD_MODULE_LIGHTING_PWM_CHANNEL_BLUE PCA9685_CH1
#define PEAPOD_MODULE_LIGHTING_PWM_CHANNEL_CAMERA PCA9685_CH2
#define PEAPOD_MODULE_LIGHTING_PWM_FQA I2CIP_FQA_CREATE(PEAPOD_WIRENUM, PEAPOD_MODULENUM_LIGHTING, 0, I2CIP_PCA9685_ADDRESS)

#define PEAPOD_MODULE_LIGHTING_ADC_CHANNEL ADS1115_CHANNEL_0
#define PEAPOD_MODULE_LIGHTING_ADC_FQA I2CIP_FQA_CREATE(PEAPOD_WIRENUM, PEAPOD_MODULENUM_LIGHTING, 0, I2CIP_ADS1115_ADDRESS)

#define PEAPOD_MODULE_LIGHTING_ADC_DELTA 100
#define PEAPOD_MODULE_LIGHTING_PWMCYCLE_DELTA 2500
#define PEAPOD_MODULE_LIGHTING_DELTA 86400000 // 24 hours
#define PEAPOD_MODULE_LIGHTING_PHASE 57600000 // 16 hours on
#define PEAPOD_MODULE_LIGHTING_DUTY_RED 0.5 // 50% Duty Cycle
#define PEAPOD_MODULE_LIGHTING_DUTY_BLUE 0.5 // 50% Duty Cycle
#define PEAPOD_MODULE_LIGHTING_DUTY_CAMERA 0.5 // 50% Duty Cycle

namespace PeaPod {
  extern FSM::Variable adc_voltage;
  extern FSM::Variable pwm_lighting_red;
  extern FSM::Variable pwm_lighting_blue;
  extern FSM::Flag enable_lighting;
  extern FSM::Flag enable_camera;

  template <i2cip_fqa_t F, unsigned char C> void callback_adc_read(bool _, const FSM::fsm_timestamp_t& __);
  void callback_adc_voltage(bool _, const FSM::Number& v);

  class PeaPodModuleLighting : public PeaPodModule {
    private:
      FSM::IntervalCallback* interval_adc = nullptr;
      FSM::IntervalCallback* interval_lighting_on = nullptr;
      FSM::IntervalCallback* interval_lighting_off = nullptr;
      // FSM::IntervalCallback* interval_pwmcycle = nullptr;

      template <unsigned char P> static void callback_lighting_modulate(bool _, const FSM::Number& pwm);

      static void callback_lighting_gate(bool _, const bool& onoff);

      static void callback_lighting_camera(bool _, const bool& onoff);

      // static void callback_pwm_cycle(bool _, const FSM::fsm_timestamp_t& __);

    public:
      PeaPodModuleLighting(bool chronoCallbacks = true);

      ~PeaPodModuleLighting();
  };
}

#include <light.tpp>

#endif

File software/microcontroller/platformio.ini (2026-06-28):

; PlatformIO Project Configuration File
;
;   Build options: build flags, source filter
;   Upload options: custom upload port, speed and extra flags
;   Library options: dependencies, extra library storages
;   Advanced options: extra scripting
;
; Please visit documentation for the other options and examples
; https://docs.platformio.org/page/projectconf.html

[platformio]
default_envs = feather

[env:nano]
platform = atmelavr
framework = arduino
board = nanoatmega328new
test_build_src = true
monitor_speed = 115200
lib_deps = bblanchon/ArduinoJson@^7.2.1
lib_extra_dirs = lib/I2CIP/lib

[env:feather]
platform = espressif32
framework = arduino
board = adafruit_feather_esp32_v2
monitor_speed = 115200
test_build_src = true
test_speed = 115200
lib_deps = bblanchon/ArduinoJson@^7.2.1
monitor_filters = esp32_exception_decoder
lib_extra_dirs = lib/I2CIP/lib

[env:gpionano]
platform = atmelavr
framework = arduino
board = nanoatmega328new
upload_protocol = custom
upload_command = sudo avrdude -p $BOARD_MCU -C avrdude_gpio.conf -c peapod -v -U flash:w:$SOURCE:i
monitor_speed = 115200
monitor_port = /dev/ttyS0
test_build_src = true
test_speed = 115200
test_port = /dev/ttyS0
lib_deps = bblanchon/ArduinoJson@^7.2.1
lib_extra_dirs = lib/I2CIP/lib

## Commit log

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2021-02-11 Main Script and Arduino Interfacing
    Created main PeaPod.ts script
    Created PeaPod-Arduino serial interface - performs revision checks, delivers instructions, and returns data using a callback+pipe
    Created PeaPod Arduino interface simulator - generates data according to a config object (min, max) on a fixed interval for each dataset
    Fixed package/gitignore/etc.
2021-02-25 Hardware and Assembly
    [components_digikey.csv, scale_lower.stl, scale_upper.stl]
2021-05-25 Schematic, BOM V0.1
    [bom.csv]
2021-06-03 Added customer reference R1 in BOM
    [bom.csv]
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2021-06-07 Renamed Aero to Humidification
    [bom.csv]
2021-06-07 Renamed Files
    [humidification_bom.csv]
2021-06-16 Added BoM: Templates, PR Checklist
    [bom_template_manufacturing.csv, bom_template_purchase.csv]
2021-06-16 BoM Initial Commit
    [frame_bom_manufacturing.csv, housing_bom_manufacturing.csv, housing_bom_purchase.csv]
2021-06-16 Purchase BOM Template: Added Description
    [bom_template_purchase.csv]
2021-06-16 Added L Brackets
    [housing_bom_manufacturing.csv]
2021-06-16 Renamed Manufacturing to Fabrication
    [housing_bom_fabrication.csv]
2021-06-16 BoM Template: Renamed Manu. to Fabrication
    [bom_template_fabrication.csv]
2021-06-16 Added All Fabricated Parts
    [housing_bom_fabrication.csv]
2021-06-16 Added everything from previous BoM
    All parts excluding 3D printed parts.
    [housing_bom_purchase.csv]
2021-06-16 Changed all files extensions to stl
    [housing_bom_fabrication.csv]
2021-06-16 Added 3D Models for Fabrication
    [ExtrusionCap.stl, GrowPlateQuarter.stl, GrowPlateWasher.stl, LBracketA.stl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]
2021-06-16 Added pump, tank, solenoid.
    [aeroponics_bom_purchase.csv]
2021-06-16 Added tubing, connectors, nozzles.
    [aeroponics_bom_purchase.csv]
2021-06-17 Moved stuff to the right spot
    [aeroponics_bom_purchase.csv]
2021-06-23 Added Couplers, Etc. to BoM
    [aeroponics_bom_purchase.csv]
2021-06-24 Migrated Existing Sensors Hardware, Software
    All PeaPod Arduino code moved to sensors software
    Moved libraries to /src/ subdir
    [scale_lower.stl, scale_upper.stl, sensors_bom_digikey.csv]
2021-06-27 BoM Update
    Removed extra info, dollar signs, URL extensions
    Added 1/4 OD tubing
    [aeroponics_bom_purchase.csv]
2021-06-27 Restructured, Created Readme w/ Assembly
    [aeroponics_bom_purchase.csv]
2021-06-30 Resized Metric Holes, Changed Nozzle Mount
    [GrowPlateQuarter.stl, GrowPlateWasher.stl, LBracketA.stl, LBracketB.stl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]
2021-06-30 Nozzle Mount BoM Adjustment
    added mounting clamp
    [housing_bom_purchase.csv]
2021-06-30 BoM Revision
    [housing_bom_purchase.csv]
2021-07-01 added pressure sensor and fittings
    [aeroponics_bom_purchase.csv]
2021-07-03 Fixed Part Sizings
    [ExtrusionCap.stl, SealStrip.stl]
2021-07-03 BoM Formatting
    [aeroponics_bom_purchase.csv]
2021-07-03 Removed Old FPT Coupler
    [aeroponics_bom_purchase.csv]
2021-07-03 Created Component BoM for Sensor
    [aeroponics_bom_components.csv, aeroponics_bom_purchase.csv]
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2021-07-06 Removed Center from "A"
    Better printing success rate
    [ExtrusionCap.stl]
2021-07-07 Snap-Fit Extrusion Caps
    New chamfered centre pin
    [ExtrusionCap.stl]
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2021-07-30 Cut Constraints
    moved estimates to appendix
    fixed citations
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2021-08-17 Updated for Door
    [housing_bom_purchase.csv]
2021-09-13 Squashed commit of the following:
    commit edd2e320934a10050e6a734e7f221cd0c52407a9
    Author: Jayden Lefebvre <jayden.lefebvre55@gmail.com>
    Date: Mon Sep 13 15:41:54 2021 -0400
    Delete actuator class
    commit 215b883cccbcfc56583e870d5dec005db6cc2654
    Merge: 85135fe 7164cfe
    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
    [Gerber_BoardOutline.GKO, Gerber_BottomLayer.GBL, Gerber_BottomSolderMaskLayer.GBS, Gerber_Drill_NPTH.DRL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]
2021-09-13 New PCB Design
    BoMs, Fusion/Eagle .sch and .brd files, pngs of both, and FBX PCB models
    [Gerber_BoardOutline.GKO, Gerber_BottomLayer.GBL, Gerber_BottomSolderMaskLayer.GBS, Gerber_Drill_NPTH.DRL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]
2021-09-27 Siphon Injector, BoM updates
    [SiphonInjector.stl, aeroponics_bom_components.csv, aeroponics_bom_fabrication.csv, aeroponics_bom_purchase.csv]
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2021-10-13 BoM Updates
    Finished https://github.com/UpRouteFoundation/PeaPod/issues/50#issuecomment-877507976
    Made sure older listings matched CAD and prototype
    Left the ones that were going to be outdated eventually
    [aeroponics_bom_purchase.csv]
2021-10-13 Housing BoM Update
    [DiagonalBracket.stl, ExtrusionCap.stl, InsulationMount.stl, LBracket.stl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]
2021-10-22 Added PCB BoM
    [lighting_purchase_bom.csv]
2021-10-25 Lighting Boards V0.2
    [copper_bottom.gbr, copper_top.gbr, drill_1_16.xln, gerber_job.gbrjob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]
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2021-10-26 Added Locking DC Barrel Jack
    [copper_bottom.gbr, copper_top.gbr, drill_1_16.xln, gerber_job.gbrjob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]
2021-10-26 Added Supporting Files for V0.2
    SCH, BRD, and PNG for both
    Also FBX models
    [lighting_led.brd, lighting_led.sch, lighting_power.brd, lighting_power.sch]
2021-10-27 New Lighting PCB Mounts
    New STLs, mounting BoMs
    [LightingLEDMount.stl, LightingPowerMount.stl, housing_bom_fabrication.csv, housing_bom_purchase.csv]
2021-10-27 Added Aeroponics Input Connectors
    [aeroponics_bom_purchase.csv]
2021-10-28 Structure Overhaul
    [Cartridge.stl, CartridgeLid.stl, DiagonalBracket.stl, ExtrusionCap.stl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]
2021-11-15 Lighting V0.3
    Fixed daisy-chaining "mirroring" problem
    Made DC jack footprint holes smaller (3.3mm->3.1mm dia.)
    Made Molex support pads NC
    Minor routing updates
    Updated silkscreen text
    [copper_bottom.gbr, copper_top.gbr, drill_1_16.xln, gerber_job.gbrjob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]
2021-11-16 Removed Panel Mounts
    [InsulationMount.stl, housing_bom_fabrication.csv]
2021-11-16 Updated BoM References
    Also removed seal strip stl
    [SealStrip.stl, aeroponics_bom_components.csv, aeroponics_bom_fabrication.csv, dehumidification_bom_fabrication.csv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]
2021-11-16 Added Feet
    [Feet.stl, housing_bom_fabrication.csv, housing_bom_purchase.csv]
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2021-11-26 Lighting V0.4
    FINALLY fixed the connector flipping error (hint: pin 1 goes to pin 6 EVERY TIME)
    Flipped LED series order (blue on bottom)
    More "bus"-like routing on power PCB
    Updated version number text on PCBs
    [copper_bottom.gbr, copper_top.gbr, drill_1_16.xln, gerber_job.gbrjob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]
2021-11-26 Standardized Trace Width
    10mil on all traces (~8C rise at .7A)
    [copper_bottom.gbr, copper_top.gbr, drill_1_16.xln, gerber_job.gbrjob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]
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2022-01-16 BoM: Alt. Molex Socket
    [lighting_component_bom.csv, lighting_led_component_bom.csv, lighting_power_component_bom.csv]
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2022-02-01 Power V0.5 - Module Update
    Replaced discontinued module (LDD-H) with SMD package variant (LDD-HS; same functionality)
    Board and mount resized, components repositioned
    Added PWM pull-down resistors
    [copper_bottom.gbr, copper_top.gbr, drill_1_16.xln, gerber_job.gbrjob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]
2022-02-04 Peltier Driver V0.1
    [copper_bottom.gbr, copper_top.gbr, drill_1_16.xln, gerber_job.gbrjob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]
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2022-03-09 Added Components
    Voltage divider resistors, relay coil resistors
    [thermoregulation_driver_components_bom.csv.csv]
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2022-03-25 Cleanup
    * Refactored "power" to "driver", incl brd, brd png, and gerber
    + Readme ordering details
    [copper_bottom.gbr, copper_top.gbr, drill_1_16.xln, gerber_job.gbrjob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]
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2022-04-06 Aeroponic Container
    * Updated plumbing diagram, BoM
    - Removed old "assembled" photo
    * New tray mounts
    * Renamed other housing fabrication files
    - Removed siphon injectors
    [ExtrusionCap.stl, SiphonInjector.stl, TrayMountA.stl, TrayMountB.stl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]
2022-05-02 Dosage Pump
    [aeroponics_dosagepump_components_bom.csv, aeroponics_dosagepump_fabrication_bom.csv, aeroponics_dosagepump_purchase_bom.csv, aeroponics_supply_purchase_bom.csv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]
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2022-05-30 Aeroponic Container
    [aeroponics_tray_purchase_bom.csv]
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2022-05-30 Materials: Housing
    [housing_bom_fabrication.csv, housing_bom_purchase.csv]
2022-05-30 Materials: Aeroponics
    split housing (shell, grow and lighting trays)
    table formatting
    [aeroponics_supply_purchase_bom.csv, aeroponics_tray_purchase_bom.csv]
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2022-05-30 Materials: Thermoregulation pt. 2
    [copper_bottom.gbr, copper_top.gbr, drill_1_16.xln, gerber_job.gbrjob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]
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2022-05-30 Materials: Lighting
    [lighting_driver_component_bom.csv]
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2025-08-29 Docs WIP
    [microgreens_bom_components.csv, microgreens_bom_purchase.csv, template_bom_components.csv, template_bom_purchase.csv]
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2026-06-14 Updated Motherboard
    [automation.brd, automation.sch, automation_bom_components.csv]
2026-06-17 Automation Gerber, Readme
    [automation.brd, automation.sch, copper_bottom.gbr, copper_top.gbr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]
2026-06-28 Lighting Overhaul
    [copper_bottom.gbr, copper_top.gbr, drill_1_16.xln, gerber_job.gbrjob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]

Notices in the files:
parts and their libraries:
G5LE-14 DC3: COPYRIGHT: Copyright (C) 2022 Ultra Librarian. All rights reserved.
